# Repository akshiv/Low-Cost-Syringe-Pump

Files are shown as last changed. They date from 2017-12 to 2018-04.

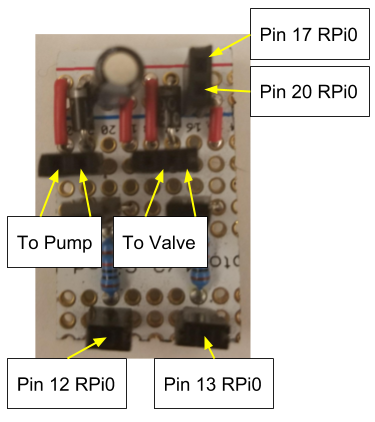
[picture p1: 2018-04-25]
documentation/figures/Driver Connections.png

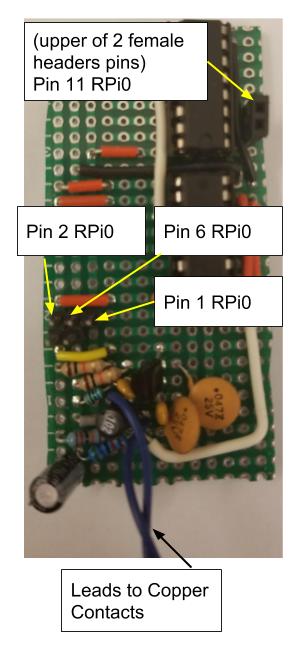
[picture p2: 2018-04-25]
documentation/figures/Oscillator Connections.jpg

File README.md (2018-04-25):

# Low Cost Syringe Pump
Repo for the ENPH 479 syringe pump project

## Introduction
This readme document serves as a guide to future development of the low cost syringe pump project. This document will outline the details of basic use and development. Further details on design approach and project motivation can be found in the engineering recommendation report for the project, which is located in this same git repository. 

## Getting Started with The Pump
The pump employs a Raspberry Pi Zero for controlling and powering all components. The first step for project development is to configure the Raspberry Pi for headless operation so that it can be controlled via Wifi. The pump’s electromechanical systems can then be setup, and the pump code can be ran on the raspberry Pi to operate the pump.

### Raspberry Pi Setup
The system uses a raspberry pi zero with pre-configured software loaded on the SD card so that the files needed to run the pump are available. 

To control the Raspberry Pi over wifi, the system must be setup to access the local wifi network by following step 3 of this tutorial document.

One can then connect to the Raspberry Pi using SSH either through the terminal on Linux, or by using a tool like PuTTY on Windows. Connect to the Pi at the adress pi@raspberrypi.local on port 22. The default password is raspberry

### Pump Setup
To connect all electrical connections in the pump system, follow this raspberry pi pinout chart, and the following diagrams which show the connections for the two pump circuit boards (the oscillator on the left and motor driver on the right).

The pneumatic connections between the pump, valve, and drive syringe must also be connected using a tee-junction. Then all components can be arranged within the 3d printed chassis and the two halves of the chassis can be secured together with elastic bands. 

### First Run

## Potential Future Projects 

### Feedback system design for a Low-Cost Syringe Pump for Global Medicine

#### Project Objectives, Background and Scope
The low cost syringe pump project is aimed at providing cheap accessible anesthesia in low resource surgical environments. The system uses capacitive contact feedback to improve accuracy and precision in lieu of mechanically precise components to bring down cost. An initial prototype, with a working capacitive contact/oscillator system exists but needs to be improved for both performance and reliability. The project will focus on designing the lowest cost oscillator, which can achieve the performance targets, improving the control loop so that the system can be used in a mission critical settings, and testing the reliability of both systems together. 

#### Design and Analysis
Design
Best possible oscillator used to amplify a variable capacitor scheme
Robust control loop which matches a flow rate based on oscillator input, desired pump rate, and current infusion status
Time permitting, sealing and packaging of electronic component inside of chassis for field deployment

Analysis
Reliability testing for both the control loop and the oscillator 
Edge case mitigation for errors/anomalies in clinical use

#### Expected Technical Background
Ideal candidates for this project will have an interest in circuit and control design. They will be comfortable using standard electrical prototyping equipment. They will be comfortable working in a Linux environment and writing code in C. 

### Smartphone Interface Development for a Low-Cost Syringe Pump for Global Medicine

#### Project Objectives, Background and Scope
The low cost syringe pump project is aimed at providing cheap accessible anesthesia in low resource surgical environments. The system uses capacitive contact feedback to improve accuracy and precision in lieu of mechanically precise components to bring down cost. To make the device as useful as possible we need it to be both powered by and operable using a smartphone. To achieve there needs to be an app which can allow an operate to set an infusion rate and volume and also receive feedback on the process. The smartphone will need to send this information via USB On the Go to a Raspberry Pi Zero, which will use it to actually drive the pump. Ideally, the app will allow phones to be swapped mid-procedure to allow for more lengthy infusions.

#### Design and Analysis
Design:
Setup a communication protocol using USB OTG, Android, and a Raspberry Pi Zero
Design an application which easily allows an operator to control and monitor an infusion process 
Create a system to allow the infusion to be carried out on multiple smartphone devices 

Analysis:
Assess reliability in case of various software/hardware failure on the smartphone side
Find edge cases present in the clinical environment and work to mitigate them
Reduce power consumption to make the circuitry last

#### Expected Technical Background
Ideal candidates for this project will understand development for Android devices, and be resourceful when working with communications devices.

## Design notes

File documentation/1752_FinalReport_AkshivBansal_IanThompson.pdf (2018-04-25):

## Development of a Low-Cost Syringe Pump for Low-Resource Anesthesia

## Akshiv Bansal Ian Thompson

## Project Sponsors: Dr. Mark Ansermino Dr. Guy Dumont

Applied Science 479
Engineering Physics
The University of British Columbia January 8th, 2018

Project Number: 1752

# Preface

There are no confidentiality considerations when reading this report. We thank the members of

the UBC Digital Health Innovation Lab, especially Dr. Mark Ansermino, Dr. Guy Dumont, Dr.

Richard Merchant, and Dr. Chris Peterson, for their support in this project.

Executive Summary Word Count: 235

Main Body Word Count: 3790

Akshiv Bansal | Ian Thompson

# Executive Summary

Safe surgical care is an essential medical resource which is unavailable to billions of people in

developing nations. Intravenous anesthesia plays a critical role in surgery, however conventional

syringe pumps are too expensive for widespread use in low-resource settings. To address this

issue, we developed a low-cost syringe pump using less than $25 of components. To meet the

demands of surgery, we aimed to achieve an accuracy of ±15% at drug delivery rates of 10-200

mL/hr.

The syringe pump design employs a simple 3D printed chassis, which holds two syringes back-

to-back. An air pump and valve drive one syringe, forcing anesthetic from the other syringe. Our

solution substitutes expensive precision components for feedback-based control. Inlaid copper

strips capacitively sense changes in the syringe volume, and a Raspberry Pi Zero uses this

feedback to control pumping and deliver anesthetic smoothly. The entire system runs from a

powered USB connection.

Testing over a wide range of flow rates, we found the pump met the design specifications for

infusion rate accuracy. This testing employed an analytical balance to track the flow of water

from the pump. These results demonstrate the viability of feedback-based syringe pump design

and provide a foundation for future development. Further refinement and validation of the

control algorithm will improve robustness and accuracy. Careful consideration of the surgical

environment and consultation with healthcare providers will help ensure successful deployment

of the device in field trials.

# Table of Contents:

Mechanical Drawings of Pump Chassis | 32
Connection Diagrams for System Setup | 33
Software Information for Project | 35

## List of Figures

Figure 1: System Overview for Feedback and Control | 9
Figure 2: Mechanical Chassis Design | 10
Figure 3: Electrical schematic layout of the Colpitts variable frequency oscillator | 11
Figure 4: Software Control Flow Chart | 13
Figure 5: Testing Setup for evaluating pump performance | 14
Figure 6: Oscillator Output Waveforms | 15
Figure 7: Capacitive feedback response linearity | 16
Figure 8: Syringe pump test results for a variety of flow rates | 17
Figure 9: Proposed UI for Android phone development | 25
Figure 10: Mechanical Drawing for Pump Chassis | 32
Figure 11: Colpitts Oscillator PCB with labelled connections | 33
Figure 12: Motor Driver PCB with labelled connections | 34

## List of Tables

Table 1: Summary of project expenses | 22
Table 2: General Bill of Materials | 27
Table 3: Oscillator Bill of Materials | 29

## List of Abbreviations:

FPGA | Field Programmable Gate Array
DHIL | Digital Health Innovation Lab (Project Sponsors’ Lab)
IC | Integrated Circuit
RPi0 | Raspberry Pi Zero

# Introduction

## Background and Significance

Anesthesia is an essential medical service, which induces paralysis or unconsciousness in the

patient, allowing for easier surgery and alleviating pain for patients. Intravenous anesthetics are

administered through injection into the patient. They are common and well-understood.

Conventional medical practice in developed nations employs a motor-driven lead screw to force

a precise flow of anesthetic from a loaded syringe.

In Essential Surgery, the International Collaboration for Essential Surgery outlines 44 procedures

that would avert 1.5 million deaths every year in developing countries, many of which rely on

pump-based IV anesthesia [1]. Existing commercial solutions are far too expensive for these

settings, costing $1000 or more. By designing a low-cost anesthetic pump, we aim to make these

critical procedures more available. Previous pump designs have showed promise for addressing

this need but have been inadequate in accuracy [2], versatility [3], or total cost [4]. We believe

that an innovative, closed-loop approach will allow us to address the need for accuracy while

maintaining a low device cost.

There are unique challenges we faced when designing a syringe pump for use in developing

nations, and constraints of the low-resource surgical environment have informed our project

goals and design decisions. Our primary constraint was cost. We focused on using commonly

available components and simple methods of fabrication and construction. We ensured that the

system will be cost-effective at initial deployment by choosing the most effective design for a

scale of tens to hundreds of pump units.

Another constraint is the lack of reliable, clean power in many surgical environments. We

designed our system to be powered from a mobile phone, which is a widespread and reliable

source of power. We designed our pump to have low latent power consumption, and to pull no

more instantaneous power than a typical mobile phone can provide. We considered other

variabilities in operating environments. Finally, we aimed to create an open source and easily

adoptable design. We created simple designs using common tools and programming languages, with the intent of making build plans available to groups who want to use the device. Versatility

in syringe size was considered to allow adaptation to different medical procedures.

## Project Objectives

1. Design of a syringe pump for approximately $25 in components or less
2. Demonstration of a syringe pump, which delivers anesthetic at a specified flow rate

between 10-200 ml/hour with an accuracy of ±15%.

3. Design of an electrical power and user interface system to allow the pump to be operated

and powered directly from an Android mobile phone.

4. Design of mechanical and electrical systems to ensure the syringe pump is operable

without expertise, while being tolerant to light impacts, dust, water, and variations in the

environment.

5. Appealing implementation of the system so it can be demonstrated to potential sources of

funding or other parties interested in supporting the project.

## Report Scope and Organization

To effectively deliver anesthesia, we sought to build a closed-loop, pneumatically-actuated

pump, with a capacitive feedback mechanism. We started the project with a syringe pump

concept, which worked using an FPGA and a specific syringe model. Throughout the project we:

designed and built a new chassis to work with any generic syringe, created a new electronic

measurement and control system using feedback electronics and a Raspberry Pi Zero computer

(RPi0), and validated the pump performance at a variety of flow rates.

The project excluded consideration of alternative feedback mechanisms, controllers, and

actuation methods. These were excluded because of time constraints and increases to the final

cost of the device. For example, the FPGA was abandoned because at the scale of our initial

device production, the chip setup would be more expensive than the RPi0 solution. These topics

will not be addressed in this report.

# Discussion

## Methods

System Design

The system is composed of three subsystems: a RPi0 controller, an air pump/valve pneumatic

actuation system, and a capacitor-controlled oscillator for feedback. The feedback system is used

to obtain information on the syringe position, which is processed by the RPi0 controller to

generate pneumatic correction to achieve proper drug delivery rates. The pneumatic corrections

are applied by actuating the air pump/valve system.

These systems are all housed in a single 3D-printed chassis to create a clean and compact

prototype. Power to run the device is provided by an Android phone. All aspects of the system

are intended to limit upfront cost and allow for use with minimal additional materials. The

intention is to deliver a kit with everything required to run the pump out of the box, save for a

soldering iron, medical tubing, a syringe, and a smartphone. Pneumatic actuation and capacitive

feedback help to reduce the material cost significantly by alleviating the need for precision

actuation components. Cost was the driving factor many design decisions, including selection of

all electronic and electromechanical components. The total cost of the project is estimated to

approximately $23.50. The RPi0 enables ease of development in C and allows a wider open-

source community to adopt and change the project.

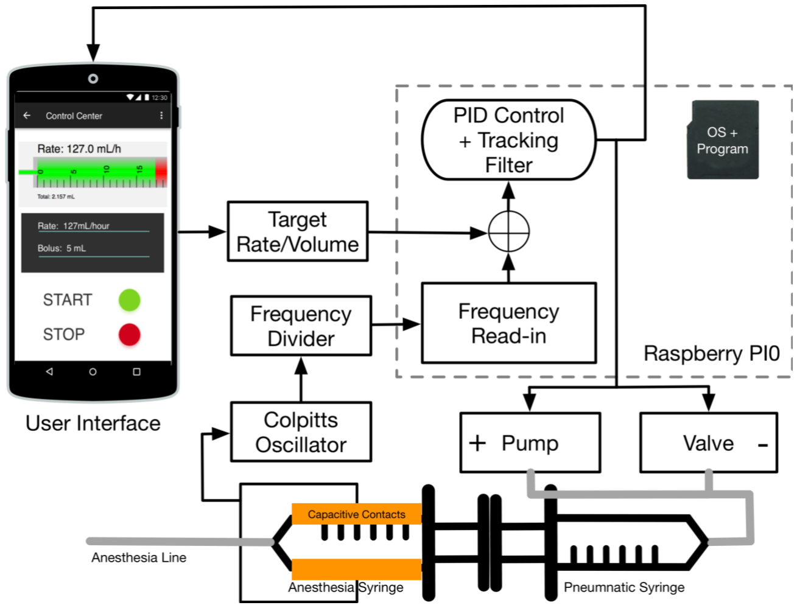
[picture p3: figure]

Figure 1: System Overview for Feedback and Control Using the smartphone, the user inputs a target infusion rate and an overall volume. The rest of the system responds to deliver anesthetic as specified. The Raspberry Pi0 takes user input and issues signals to the pump/valve combination, driving the passive pneumatic syringe plunger forwards. The pneumatic syringe presses the plunger of the active anesthesia syringe, which dispenses the drug solution through the anesthesia line. Copper contacts on either side of the syringe form a capacitor, which set the frequency of a Colpitts oscillator. This signal is frequency divided and read into the Raspberry PI0 as feedback for a PID control algorithm, which in turn actuates the pump/valve system

Mechanical Design

The chassis is designed to house all of the components and provide resistance to impact. To this

end, the design focused on making an economically printable enclosure, with a setup to allow all

electronics to be installed in the body, without need for electronics access or adjustments during

operation.

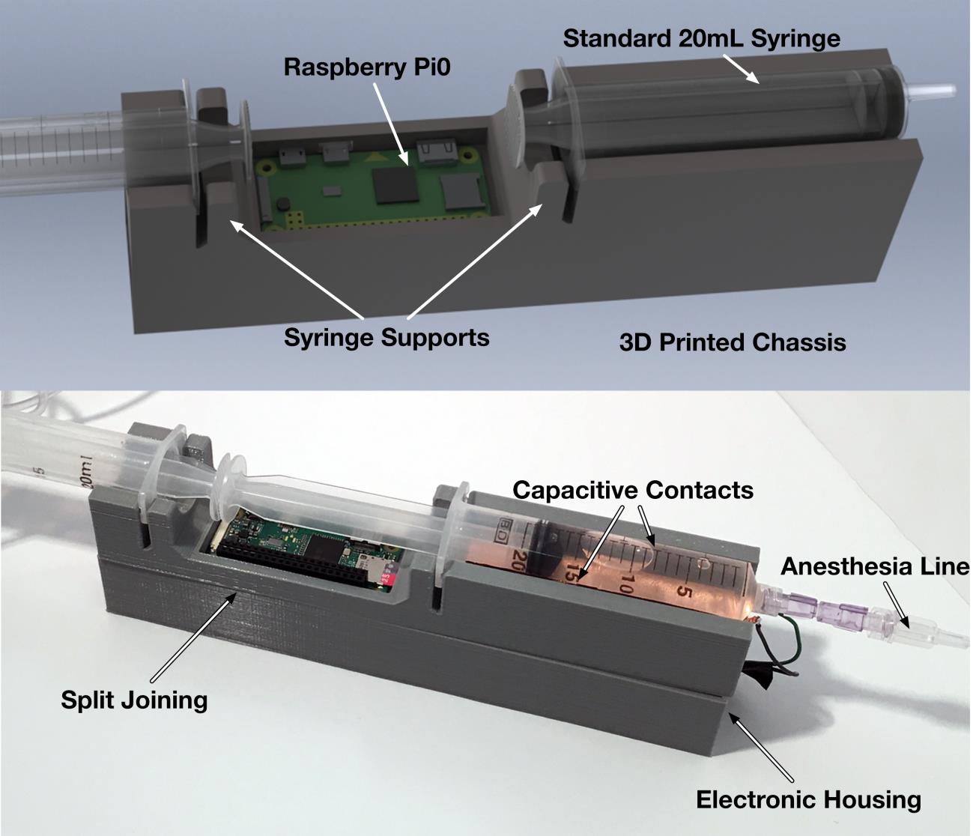
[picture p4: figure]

Figure 2: Mechanical Chassis Design The chassis design is based on original work done by the project sponsors. This chassis has built in capacitive contact pads, such that generic anesthetic syringes can be used, and a clean surgical setting maintained. All of the electronics are housed inside the chassis, and the Raspberry Pi0 sits below the syringes (normally covered). The split in the prototype was introduced to simplify 3D printing, and the two halves are joined. The syringe supports are necessary to deal alternating stress from syringe installation and operation.

Electrical Design

To accurately detect small capacitance changes due to syringe actuation, we constructed a

capacitance-controlled variable frequency oscillator. We selected the Colpitts oscillator topology

(shown in Figure 3), which produces large variations for small capacitance changes, and uses

readily available, affordable components. Each oscillation must be accurately detected by the

RPi0, thus we tuned component values to adjust the signal amplitude and frequency to match the

RPi0’s capabilities. We found a maximum detectable frequency of 18kHz for our read-in method

on the RPi0, limited by I/O bus speed. A two-stage, 18-bit frequency divider reduces the

oscillation frequency to approximately 100 Hz, lowering the computational demand with

minimal component cost.

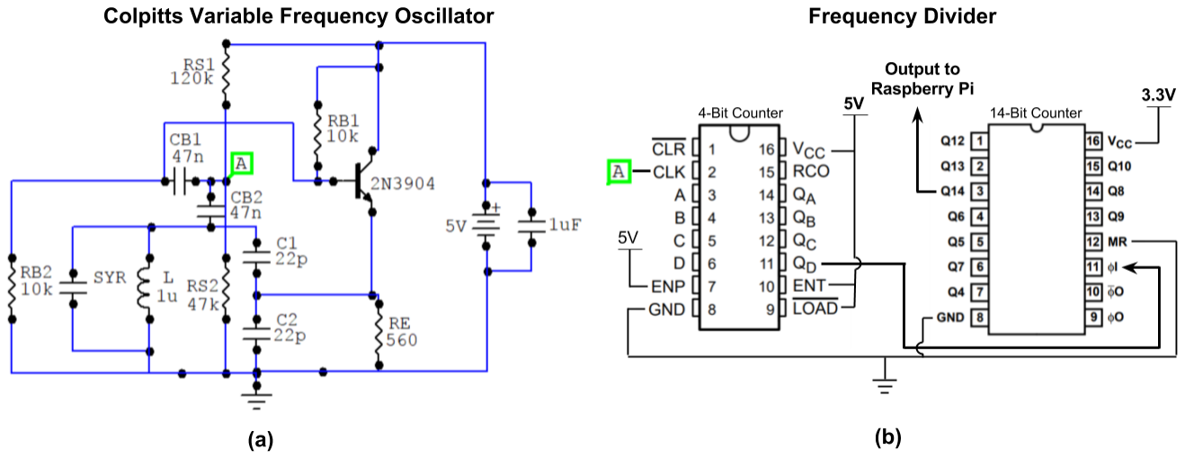
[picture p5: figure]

Figure 3: Electrical schematic layout of the Colpitts variable frequency oscillator
(a) A variable frequency colpitts oscillator topology is used to create a sinusoidal oscillation at point A (labelled with a green square). Variations in the syringe capacitance (labelled SYR in the diagram), change the oscillation frequency. The frequency is in the range of 30-50 MHz, set by L, C1 and C2. We selected setpoint-biasing resistors and bypass capacitors (RS1, RS2, CB1 and CB2) to center the oscillation around the correct voltage for input into a frequency divider circuit. (b) A frequency divider circuit uses a 4-bit and a 14-bit counter to divide the oscillation frequency, allowing for output to the Raspberry Pi 0. Separate Vcc for each counter are selected to ensure the correct output voltage range.

The air pump and valve are operated using general purpose input/output (GPIO) pins on the

RPi0. Since the GPIO pins have a output current lower than needed to drive the system, we

constructed a simple switching circuit using an NPN Darlington transistor to power the

components from the device power rails. The GPIO pins control switching; for logic high, the

driver circuit powers the air pump or valve with 3.3V, and for logic low, the component is

switched off.

## Flow Diagram / Algorithms

The pump control is code executed on the RPi0 and is initialized by the user providing a target

flow rate and total volume. Feedback from the syringe is monitored using an interrupt routine,

which counts oscillations for a developer specified counting interval. Shorter counting intervals

can be selected to increase response time, while longer intervals improve noise rejection. As readings are constantly generated by the feedback system, these values are compared to user

targets for flow rate.

The control system actuates the valve and air pump in response to error, increasing or decreasing

the air pump driving voltage if the syringe is lagging or leading respectively, or opening the

valve when the syringe is moving too fast. The developer can specify weights for proportional,

integral, and derivative error, as well as the threshold for releasing pressure through the valve.

These parameters can be tuned to optimize system performance. The syringe pump runs until the

feedback indicates that the system has infused the total amount desired, at which point the pump

stops and releases all pneumatic pressure. During the pumping process, the feedback readings,

pumping status, and applied valve and air pump corrections are reported for analysis. The code is

implemented in C for speed and ease of execution on the RPi0.

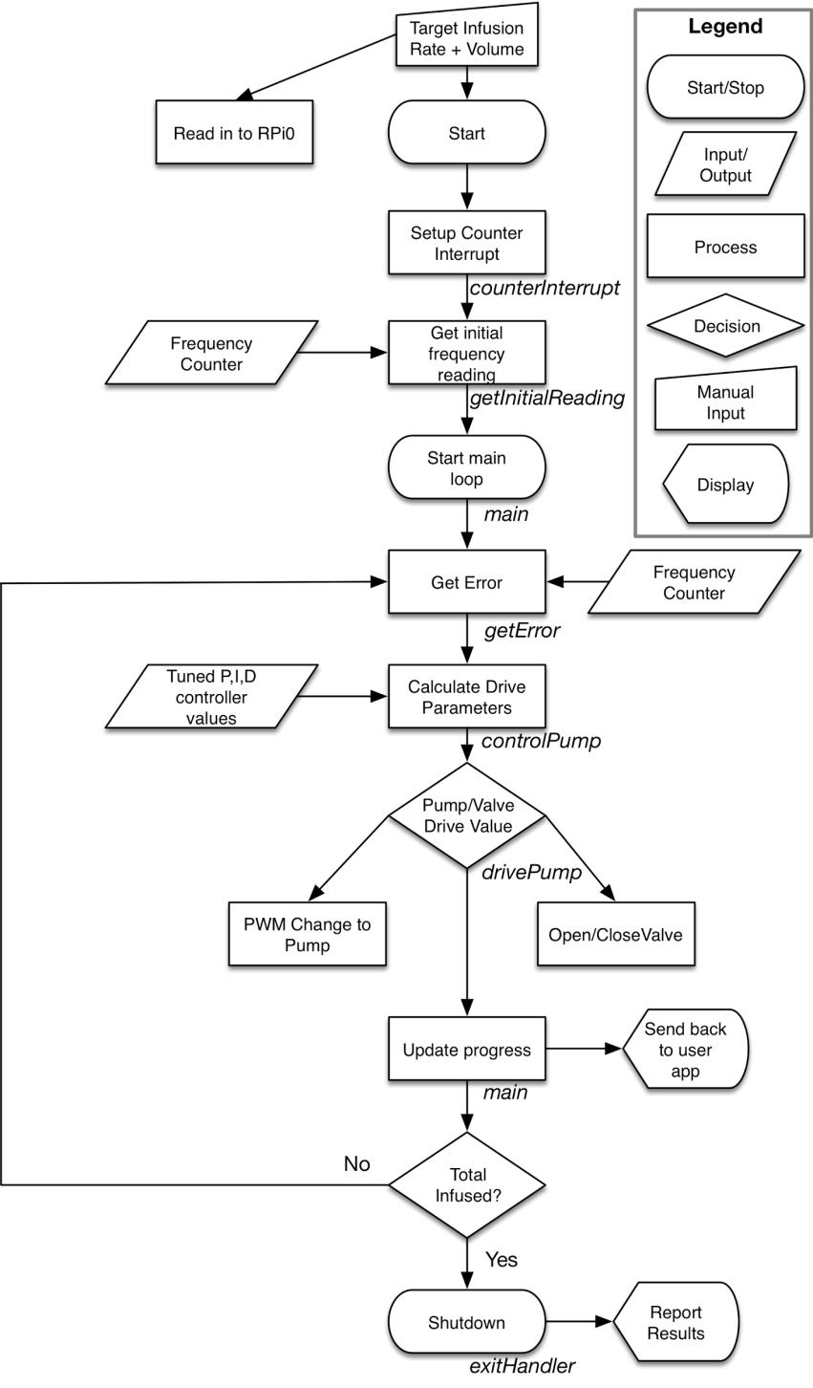
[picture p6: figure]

Figure 4: Software Control Flow Chart The software implementation on the Raspberry Pi0(RPi0) handles pump control, with an Android app serving as the user interface. After the user sets the target rate and volume, the RPi0 initializes its I/O ports, and starts to read in frequency information from the oscillator/capacitor feedback system. The system stays in its primary loop until the desired amount of drug has been infused. In the loop, the system generates an error from the difference in the current syringe position and the desired syringe position. It then uses this error, along with control parameters, to drive the pump faster or slower, release the check valve, or wait until the next update. Upon reaching the volume target or encountering an error, the system goes to the exit handler, which stops all parts of the system before reporting the result to the operator and shutting down the system.

## Experimental Equipment & Testing Protocol

We characterized the Colpitts oscillator output using an oscilloscope, powering the circuit from

the RPi0. Capacitive feedback linearity data was obtained using the same frequency counting

routine as the pump control software.

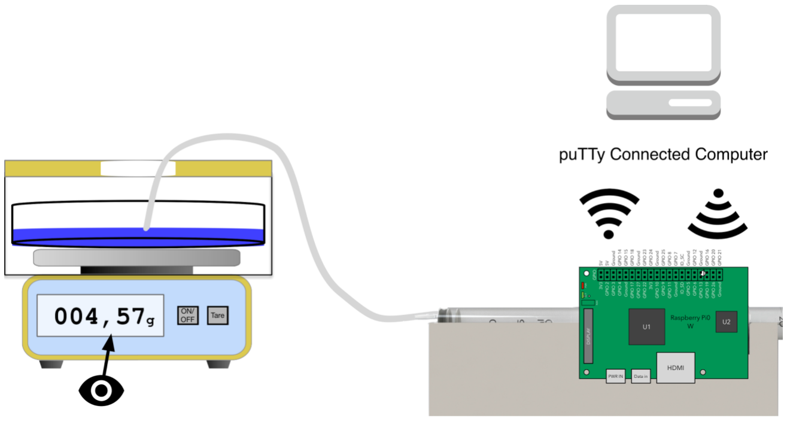
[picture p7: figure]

Figure 5: Testing Setup for evaluating pump performance We used an analytical balance to test the infusion accuracy of the syringe pump. A computer linked to the Raspberry Pi Zero (RPi0) via an SSH connection was used to issue pump commands. We tested multiple infusion rates and volumes, monitoring the progression of each infusion. We set the pump up to drip through medical tubing into a plastic dish on top of an analytical balance (Sartorius BP110). To ensure minimal evaporation and variability we zeroed the balance with 20 mL of water already in the dish and used a plastic cover to minimize airflow. The data from the display on the balance was manually recorded at 1-minute intervals. All components were powered using AC wall power with a common ground.

We took pump performance data using an analytical balance to best replicate the ISO standard

testing protocol (detailed in Appendix: ISO Standard for Syringe Pumps). This setup is less

rigorous than the standard requires but provides a useful benchmark with the apparatuses we had

available.

## Results

The output signal from the finalized Colpitts oscillator design is shown in Figure 6 along with

the frequency divided square wave, which is input to the RPi0. The circuit was powered from the

RPi0, and waveforms were collected for a typical syringe loaded with 20 mL of water. We

designed the Colpitts oscillator with small capacitive and inductive components to increase the

sensitivity to changes in the syringe capacitance. This resulted in a high oscillation frequency of

43.91 MHz measured at the oscillator output (top subfigure). This waveform is nearly sinusoidal,

with some distortion likely due to secondary resonances in the circuit. Our frequency divider was

successful in generating a low-frequency output (bottom subfigure) to trigger the RPi0, reducing

the oscillation to 116.4 Hz and rectifying the signal to a 0-3.3V square wave with minimal

distortions or noise.

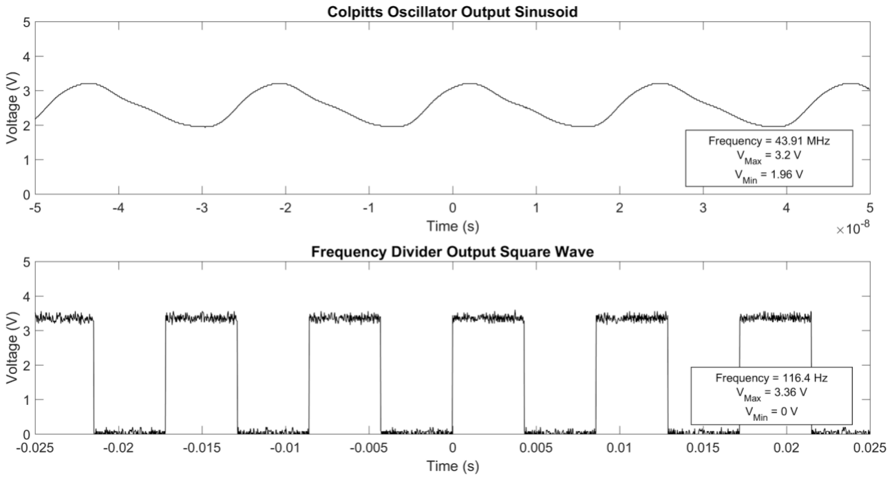
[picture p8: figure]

Figure 6: Oscillator Output Waveforms We collected output waveforms of the Colpitts oscillator before and after the frequency divider using a fully loaded syringe. Top: The signal measured at the output of the Colpitts oscillator before the frequency divider (position A in Figure 3). The initial circuit has a high frequency (43.91 MHz) output sinusoid, with a small voltage swing. Bottom: The signal measured at the final output to the RPi0. The frequency divider circuit amplifies the low-voltage sinusoid to a 0-3.3V logic signal and reduces the frequency to 116.4 Hz so that it can be properly detected by the RPi0.

To simplify the controls, we assumed the changes in feedback readings would change linearly

with the fluid volume in the syringe. To validate this assumption, we manually varied the volume of fluid through the functional range of 20mL syringe, sampling the feedback readings using the

RPi0. Performing a linear fit in MATLAB (shown in Figure 7) we find that the linear

approximation matches our data well within our desired pumping accuracy. Over the 20 mL

range of the syringe, we note a 1.84% change in the feedback readings.

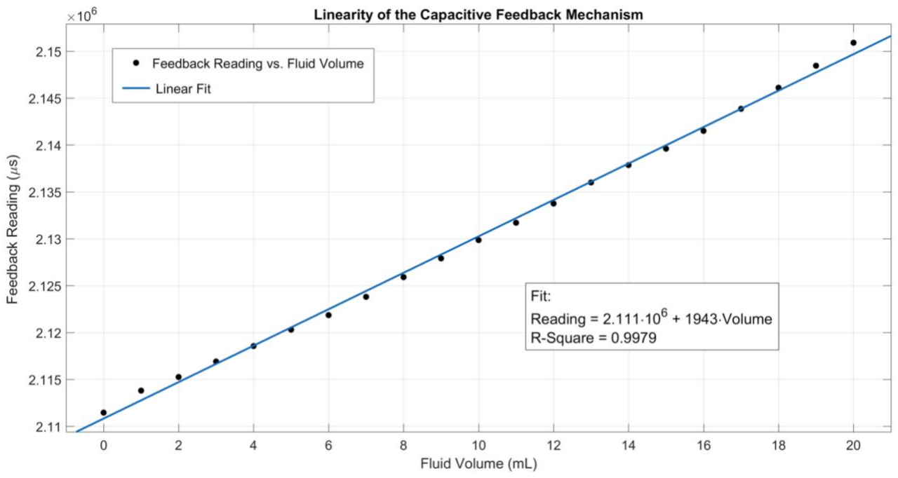
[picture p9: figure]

Figure 7: Capacitive feedback response linearity We obtained feedback readings by measuring the output period of the Colpitts variable frequency oscillator across the range of syringe fluid fill volumes. A linear fit approximates the data with an R-Square value of 0.9979, demonstrating that the feedback response is sufficiently linear over the desired operation range. This linearity can be used to simplify our control scheme and accurately approximate volumes and flow rates delivered by our system.

Using our linear feedback mechanism, we tested our PID control scheme at a variety of target

flow rates, following the procedure laid out in Experimental Equipment & Testing Protocol.

Figure 5 shows the pumping results when the pump was configured to deliver a specified total

volume of water, stopping when it sensed it had pumped that amount. The control system ran

with only proportional control, a limit of ~40% on the maximum pumping power, and a feedback

update period of approximately two seconds. At almost all time points, the pump delivered the

correct volume to within ±15% (as shown by the dotted bounds in the figure). It monitored the

total volume infused and stopped within 15% of the final target in 3 of 4 trials. During all trials,

the pump ran independently with no operator intervention.

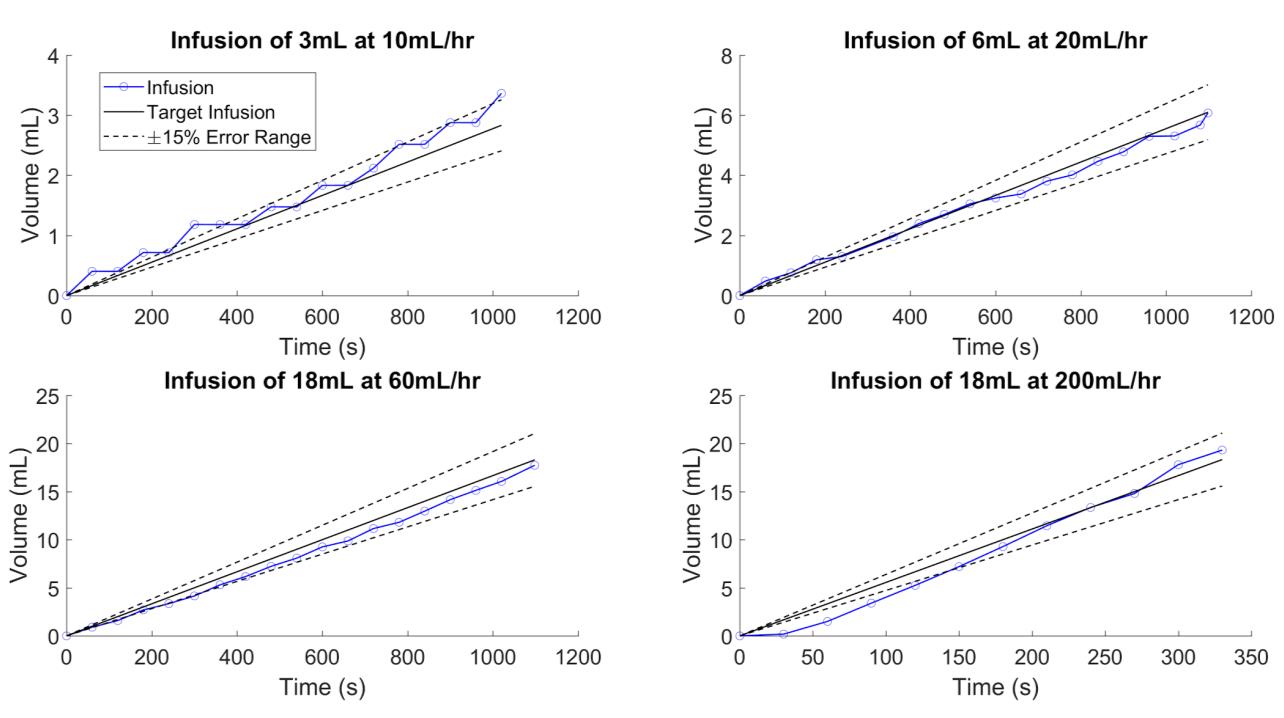
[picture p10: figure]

Figure 8: Syringe pump test results for a variety of flow rates The accuracy and smoothness of delivery for our syringe pump was tested by pumping water onto an analytical balance at a range of specified rates until a specified target volume was reached. The pump was run using proportional control, updating the control response every ~2 seconds. Flow rates of 10, 20, 60, and 200 mL/hr were selected to be representative of the full range of flow rates we expect our pump to deliver. Blue lines with circles denote the resulting volume infused by our pump (calculated assuming 1g/mL water density). The solid black line denotes the target infusion rate while the ±15% volume accuracy we aim to achieve is given by the dotted lines. Our pump meets our accuracy criteria for the majority of flow rates tested, however the presence of stiction leads to rougher performance in very slow pumping, seen in the step-like plot for 10 mL/hr infusion.

## Discussion of Results

The Colpitts oscillator outputs a reliable, well-formed signal to communicate feedback to the

RPi0, however robustness of the output can be improved. The voltage oscillation from 1.96 to

3.2 V is sufficient to be detected as input to the frequency divider circuit, however variations in

syringe capacitance or supply voltage may decrease the amplitude to under the detection

threshold. It was noted in some cases that oscillations could be lost if the syringe was improperly

placed or connections were loose. Modifications to buffer or increase the amplitude of the high-

frequency oscillator output, to improve connections, or to shield the circuit from outside static or

fields from the pump and valve may increase reliability. The counting ICs allowed for simple

reduction of frequency, making the feedback signal suitable for read-in to the RPi0, however this

leads to a reduction in precision when counting numbers of oscillations. We believe this approach is satisfactory for our control system. Increasing the precision may enable lower flow

rates to be delivered more accurately.

We can use the linearity of our feedback system response to simply and reliably monitor the

position of the syringe plunger, providing information on anesthetic flow rate and total volume

delivered. However, because the total change in readings over the range of the syringe is only

1.84%, and because we often deliver quantities smaller than the 20 mL full range, the sensitivity

of our feedback method may pose an issue. For very slow flow rates, the desired changes in

feedback readings can be very small, with noise posing a significant challenge to precision. The

15% pumping accuracy target affords some inaccuracy; however, the noise sensitivity

necessitates careful design of the control algorithm to reject noise.

The pumping performance suggests that our simple PID control algorithm is sufficient for

achieving volumetric accuracy to within 15% during infusion. While the pump exceeds the error

bounds at a few points, further testing and refinement of the control algorithm and parameters

may lead to consistent accuracy.

The pump system appears to perform best at flow rates in the middle of the specified range of

10-200 mL/hr. Because of stiction, the pump delivered anesthetic in small discrete increments,

rather than at one constant flow rate, alternating between idling and pumping somewhat rapidly.

This behavior can be seen in the step-like performance at the lowest flow rate (10 mL/hr) where

the quantity delivered per minute is so small that periods of idling last longer than one data point.

For all tests, and especially those at high flow rates, the pump showed more significant error at

the beginning of infusion, likely due to errors in estimating the initial position at startup, or

delays in pumping to an operational air pressure.

Several control system changes could be tested to correct for these issues. The lengthy feedback

update period of two seconds may be reduced to increase response time, leading to smaller step-

like increments and overall smoother behavior. However, reducing this time may lead to

increased noise sensitivity at low flow rates. Another approach to increasing smoothness may be

to lower the maximum power limit, however this may limit the pump’s ability to overcome obstructions in the line. A more robust solution could be varying the output power limit based on

the desired flow rate, as this may compensate for both the pulsing at low flow rates and the

startup inaccuracies at high flow rates. With careful adjustment and testing of the control

algorithm, we are confident that we can reliably achieve our accuracy target at all flow rates.

# Conclusions

We have successfully demonstrated a novel feedback mechanism for monitoring syringe position

during pump operation. Using capacitive sensing and a Colpitts oscillator circuit, we generate a

frequency signal, which varies with the syringe position. By demonstrating consistent linearity of

the feedback response, we showed that this system can monitor and adjust the drug delivery

process, increasing accuracy. This development represents a fundamental difference from other

syringe pumps, which rely only on precision components and open loop control.

Our pumping approach has been implemented with a compact and easy to use design. The

selection of a 3D-printed chassis allowed for easy integration of capacitive contacts, secure

housing of pump components, and design reproducibility. All components were constructed with

easily available parts, for a total parts cost of ~$23.50 (see Bill of Materials in Appendix for cost

breakdown). We believe these design choices will encourage interest in our proof of concept

device and attract potential funding or continued development efforts.

Our device achieved pumping accuracy to within ±15% over our desired range of flow rates

from 10-200 mL/hr. This performance shows that our first proof of concept merits further

development and design refinement. The main barrier to adoption of our device for clinical use is

its reliability and complexity of use, and this must be addressed going forward. Adjustments to

the control scheme may increase accuracy for low and high flow rates. Sophisticated knowledge

of the project is needed to construct and operate the device in its current state. Our

recommendations aim to finalize the device in a form more suitable for widespread use.

# Project Deliverables

## List of Deliverables

1. Mechanical and Electrical Design files
a. Includes all documentation, design work, and component lists that would be

needed to make the pump at scale (i.e. at the desired $25 price point)

b. The designs are delivered in a “manufacturing ready” form
c. Documented sufficiently to allow for greater extensions/improvements

We will deliver these files to the project sponsors. The manufacturing readiness of the project is

not as expansive as originally forecasted. Additional units will still need to be 3D printed instead

of injection molded. Electronics will need to be assembled on prototype PCB, not outsourced to

a PCB manufacturer. All electronic design files will be available in the same public GitHub

repository as the software.

2. Physical Prototype Syringe Pump
a. Delivery of a working syringe that has a volumetric accuracy of ±15% and

performs in the flow rate range: 10-200mL/h

b. The prototype has a polished design
- Electronics are not visible
- Mechanical chassis is sealed
- Design can deal with modest shocks
c. The prototype can run off an Android phone for at least 2 hours, and is operable

through simple GUI

d. Moisture and splash proofing of the pump, including protecting electronics.

The prototype meets our specified accuracy over the desired range of flow rates. The chassis is

stronger and lighter than before, all components can be nicely fit together and displayed. The

chassis is not sealed or splash-proof. While the prototype will be powered by an Android phone

after our ongoing commitments are fulfilled, it cannot yet be operated by one. We will schedule a

handoff meeting where we will give our sponsors two 3D printed bodies, one with the working

pump inside. The prototype will be setup to give demonstrations and is easily configurable for

further validation.

3. Final Documentation (including Engineering Recommendation Report)
a. Includes all design documentation and methods used
b. Includes all results from prototype validation
c. Includes a list of recommended improvements before field testing

This report meets this deliverable as intended. During the hand-off meeting we will determine if

an operating manual is required, and what its requirements are (discussed in Ongoing

Commitments).

4. Access to code developed for running the syringe pump

Our open-source GitHub repository contains readable code, instructions for compiling/building,

and allows for reproduction and modification.

## Financial Summary

Item | Quantity | Vendor | Unit Cost | Purchaser | Note
3D Printing Services | 1 Pump Chassis Print | ECE Student Services | $39.20 | Guy Dumont | Sponsor’s ECE Speed Chart
4-Bit Counter SN74F163AN | 5 | Digikey | $0.95 | Project Lab | Project lab Funds
14-Bit Counter CD74HC4060E | 5 | Digikey | $0.87 | Project Lab | Project lab Funds

Table 1: Summary of project expenses At the resolution of the project, no funds are owed between parties. All other project materials not listed below were provided by project sponsors or the engineering physics project lab but not purchased specifically for this project.

## Ongoing Commitments

1. Project debrief meeting - Akshiv & Ian, End date: Mid-Feb
- We will meet with the sponsors to demonstrate our final pump performance and

discuss the future of the project.

2. Establishing Android phone powering of syringe pump - Akshiv, End date: March 8th

- Finish development of an app to allow the pump to run from a mobile phone. The

pump should be able to run without intervention for 2 hours.

3. Creation of an operation/development manual - Akshiv & Ian, End date: April 1st
- The requirements will be determined in the handoff meeting. This work is

intended to take a maximum of one week

4. Improvements to prototyping quality - Akshiv & Ian, End date: Feb 15th
- Finishing Solidworks model to include modest sealing of chassis (12 hrs. effort)
- Clean up internal wiring and connections (6 hours effort)

# Recommendations

## 1. Better securing of syringes and other components

The chassis presently features no good mechanism to secure the syringes firmly into the chassis.

This could be done by attaching elastic bands over the syringes or some change in the

mechanical design of the chassis. Implementing this will improve the reliability of the system

and allow more reliable contact between the inlaid capacitive contacts and the syringe. Further,

the electronics within the chassis could be better secured to prevent shocks from affecting system

performance. This could be done using adhesives, slots, fasteners, or other mechanical redesigns.

## 2. Further control tuning and performance validation

The pump performance provided a valuable proof of concept, but the control system needs

refinement to increase reliability and versatility. We recommend testing the effects of shortening

the feedback response time or adjusting the maximum pump power limit based on flow rate.

These adjustments may improve the pump accuracy beyond our current limits. Repeated testing

of the pump for consistency between infusions is also valuable. The pump should also be tested

with a variety of outlet attachments on the end of the anesthetic line to simulate infusion in a

clinical setting. Significant fluid resistance or back-pressure may be introduced when a needle,

adapter, or live patient is added into the fluid line. These scenarios should be carefully

considered and tested.

The robustness of the device to real-world operating conditions should be evaluated by

introducing factors such as large temperature changes, vibrations, movement of the pump body,

and interfering electromagnetic fields (i.e. nearby motors). A successful design will be

unaffected by these factors, and these issues may necessitate mechanical or electrical

modifications. Possible failure modes and misuse during operation should be investigated, such

as power disconnection, loss of communication to the device, or accidental operator input. These

cases may lead to considerations of fail-safes in software. Testing all these possible cases will

ensure that the system is fit to be used in the clinical setting. The final validation process must be

done in consultation with low-resource health care providers.

## 3. Mobile UI

To allow full deployment of the pump in the field, an Android app to operate the pump should be

created. The scope of this project entailed creating and app to power the pump from a phone,

however we did not consider phone-based operation by a healthcare provider. This user interface

needs to enable the operator to set flow rates and target volumes, to start and stop the pump, and

to monitor anesthetic delivery.

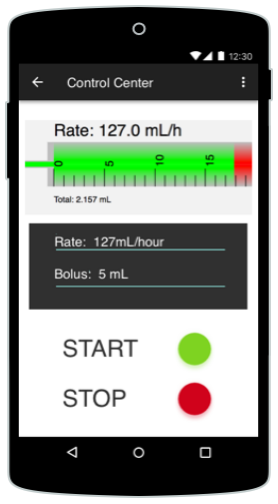
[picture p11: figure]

Figure 9: Proposed UI for Android phone development The UI allows the operator to set the target volume and infusion rate, monitor the infusion progress, and most critically start/stop the infusion.

## 4. Field Validation and Scaling Up

To develop this concept further we recommend first testing the system as designed on a small

scale in the field. The current approach using a RPi0 has been developed for optimal cost

effectiveness at small scale. After completing the recommendations, a field test with <100 units

is needed to verify the validity of using this device in a surgical setting. Once lessons learned in

field deployment have informed design modifications, the project can proceed to design for

larger scale. The device can be made more affordable and reliable through redesign for large

scale production. This involves designing a permanent PCB with an integrated FPGA, updating

the mechanical design to allow for injection molding, and creating an injection molding mold.

# References

[1] Essential Surgery. Washington (D.C.): World bank group, 2015. Print.
[2] Wijnen B, Hunt EJ, Anzalone GC, Pearce JM. Open-Source Syringe Pump Library. PLoS

ONE 2014 9(9): e107216. doi: 10.1371/journal.pone.0107216

[3] Mundle S, Regi A, Easterling T, Biswas B, Bracken H, Shekhavat DR, Durocher J, Winikoff
B. Treatment approaches for preeclampsia in low-resource settings: a randomized trial of the

Springfusor pump for delivery of magnesium sulfate. Pregnancy Hypertens. 2012;2:32–38.

[PubMed] (https://www.ncbi.nlm.nih.gov/pubmed/26104987)

[4] Juarez, Alexa et al. “AutoSyP: A Low-Cost, Low-Power Syringe Pump for Use in Low-

Resource Settings.” The American Journal of Tropical Medicine and Hygiene 95.4 (2016): 964–

969. PMC. Web. 7 Sept. 2017.
[5] CAN/CSA-C22.2 No. 60601-2-24:15; Medical electrical equipment — Part 2-24: Particular

requirements for the basic safety and essential performance of infusion pumps and controllers.

CSA Group, Mississauga ON.

# Appendices

## Bill of Materials

| Component | Vendor | Manufacturer | Source | Minimum Order | Cost (USD) | Quantity | Lead Time
1 | Solenoid Valve | EBay | bonk*town | A. | 1 | 1.59 | 0 | 2 months
| | | maaqii | B. | 1 | 1.63 | 1 | 1 month
2 | Diaphragm Pump | Aliexpress | DIT | C. | 10 Pieces | 2.419 | 0 | 20 Days
| | | SAILFLO | D. | 1 | 2.66 | 1 | 20 Days
3 | Darlington Transistor | Digikey | | E. | 100 | 0.1713 | 2
4 | 10uF E. Cap | Digikey | | F. | 1 | 0.22
5 | 1k Resistor | Digikey | | G. | 1 | 0.1
6 | Diode | Digikey | | H. | 100 | 0.0914 | 2
7 | Raspberry Pi 0 | | | I. | 1 | 5 | 1
8 | 2gb microSD | Aliexpress | | J. | 10 | 3.5 | 1 | 20 days
9 | USB Cable | | | L. | 1 | 0.6 | 1 | 40 days
10 | Oscillator Circ | | See below | | 1 | 2.85 | 1
| | | | Total: | | 16.96
| | | | Total (CAD) | | 23.50

Table 2: General Bill of Materials
A. http://www.ebay.com/itm/Mini-2-Position-3-Way-Electric-Control-Solenoid-Valve-Gas-Air-Pump-DC-

5V-6V-

HM/232395417786?_trkparms=aid%3D222007%26algo%3DSIM.MBE%26ao%3D2%26asc%3D41376%

26meid%3D6d133a7f9853490099fb0b4b447a6d6e%26pid%3D100623%26rk%3D2%26rkt%3D6%26sd%

3D122609196665&_trksid=p2047675.c100623.m-1 (http://www.ebay.com/itm/Mini-2-Position-3-Way-Electric-Control-Solenoid-Valve-Gas-Air-Pump-DC-5V-6V-HM/232395417786)

B. http://www.ebay.com/itm/Mini-2-Position-3-Way-Electric-Control-Solenoid-Valve-Gas-Air-Pump-DC-

5V-6V-MA-/112403400789?hash=item1a2bc3c855:g:rJAAAOSwIaFZFCDa (http://www.ebay.com/itm/Mini-2-Position-3-Way-Electric-Control-Solenoid-Valve-Gas-Air-Pump-DC-5V-6V-MA-/112403400789)

C. https://www.aliexpress.com/item/10pcs-New-370-DC-Air-Pump-370-motor-3V-dc-450mA-Oxygen-pump-

Mini-air-Pump/32728832531.html (https://www.aliexpress.com/item/10pcs-New-370-DC-Air-Pump-370-motor-3V-dc-450mA-Oxygen-pump-Mini-air-Pump/32728832531.html)

D. https://www.aliexpress.com/item/DC-6V-Mini-Air-Pump-Motor-For-Aquarium-Tank-Oxygen-Circulate-Durable/32830199091.html?traffic_analysisId=recommend_2088_2_90158_iswistore&scm=1007.13339.90158.0&pvid=f1234509-bb2c-48b8-8bce-fdf48264d68d&tpp=1 (https://www.aliexpress.com/item/DC-6V-Mini-Air-Pump-Motor-For-Aquarium-Tank-Oxygen-Circulate-Durable/32830199091.html?tpp=1)
E. https://www.digikey.ca/product-detail/en/fairchild-on-semiconductor/KSP13TA/KSP13TACT-ND/4314808 (https://www.digikey.ca/product-detail/en/fairchild-on-semiconductor/KSP13TA/KSP13TACT-ND/4314808)

F. https://www.digikey.ca/product-detail/en/micro-commercial-co/1N4007-TP/1N4007-TPMSCT-ND/773694
G. https://www.digikey.ca/product-detail/en/panasonic-electronic-components/ECA-1EM100B/P19522CT-ND/6109420 (https://www.digikey.ca/product-detail/en/panasonic-electronic-components/ECA-1EM100B/P19522CT-ND/6109420)
H. https://www.digikey.ca/product-detail/en/stackpole-electronics-inc/CF14JT1K00/CF14JT1K00CT-ND/1830350 (https://www.digikey.ca/product-detail/en/stackpole-electronics-inc/CF14JT1K00/CF14JT1K00CT-ND/1830350)
I. Various sources Canakit, Adafruit, etc.
J. https://www.aliexpress.com/item/10Pcs-Lot-64MB-128MB-256MB-512MB-1GB-2GB-4GB-8GB-TF-Card-Micro-SD-Cards-Micro/32819257976.html?ws_ab_test=searchweb0_0,searchweb201602_3_10152_10065_10151_10130_10068_10344_10345_10342_10343_10340_10341_10139_10307_10060_10155_10154_10056_10055_10054_10537_10059_10536_10534_10533_10532_100031_10099_10338_1 0103_10102_10052_10053_10107_10050_10142_10051_10084_10083_10080_10082_10081_ 10178_10110_10111_10112_10113_10114_9998_10312_10313_10314_10078_10079_10073-9998,searchweb201603_17,ppcSwitch_5&btsid=43012fd7-ad1e-40bb-a59ea7a1af898e6a&algo_expid=b0101ad3-e1b2-47fc-b655-c3a5fa6c4e23-0&algo_pvid=b0101ad3-e1b2-47fc-b655-c3a5fa6c4e23 (https://www.aliexpress.com/item/10Pcs-Lot-64MB-128MB-256MB-512MB-1GB-2GB-4GB-8GB-TF-Card-Micro-SD-Cards-Micro/32819257976.html)
K. https://www.aliexpress.com/item/Microusb-To-Female-USB-Host-Cable-OTG-Adapter-for-Lenovo-Xiaomi-Lg-Tablet-Android-Reader-Cabo/32670313423.html?ws_ab_test=searchweb0_0,searchweb201602_3_10152_10065_10151_10130_10068_10344_10345_10342_10343_10340_10341_10540_10139_10307_10060_10155_10154_10056_10055_10054_10539_10538_10537_10059_10536_10534_10533_100031_10099_10103_10102_10052_10053 _10107_10050_10142_10051_10325_10084_10083_10080_10082_10081_10178_10110_10111_10112_1 0113_10114_10312_10313_10314_10078_10079_10073,searchweb201603_2,ppcSwitch_5&btsid=62edbd e3-9e9e-4d37-ad84-00e080925017&algo_expid=828e3520-3206-4af5-9767-4ca5c9219ef5-0&algo_pvid=828e3520-3206-4af5-9767-4ca5c9219ef5 (https://www.aliexpress.com/item/Microusb-To-Female-USB-Host-Cable-OTG-Adapter-for-Lenovo-Xiaomi-Lg-Tablet-Android-Reader-Cabo/32670313423.html)

Oscillator Circuit Bill of Material
| Component | Vendor | Source | Minimum Order | Cost (USD) | Quantity
1 | 10k Resistor | Digikey | A. | 250 | 0.01768 | 2
2 | 120k Resistor | Digikey | B. | 100 | 0.0232 | 1
3 | 56k Resistor | Digikey | C. | 100 | 0.0232 | 1
4 | 560 Resistor | Digikey | D. | 100 | 0.0232 | 1
5 | 47nF Cap | Digikey | E. | 100 | 0.1079 | 2
6 | 22pF Cap | Digikey | F. | 100 | 0.0985 | 2
7 | 2N3904 NPN BJT | Digikey | G. | 100 | 0.139 | 1
8 | 1uH Inductor | Digikey | H. | 100 | 0.349 | 1
9 | 1uF Ceramic Cap | Digikey | I. | 100 | 0.135 | 1
10 | 2 pos Header pin | Digikey | J. | 100 | 0.0817 | 1

11 PCB (1.5"x1') | | Chopped from Projectlab | | 1 | 0.5 | 1
12 | 4Bit Fast Counter | Digikey | K. | 100 | 0.6074 | 1
13 | 14 Bit Counter | Digikey | L. | 100 | 0.5282 | 1
| | | | Total: | 2.85806
Table 3: Oscillator Bill of Materials
A. https://www.digikey.ca/product-detail/en/stackpole-electronics-inc/CF14JT10K0/CF14JT10K0CT-ND/1830374 (https://www.digikey.ca/product-detail/en/stackpole-electronics-inc/CF14JT10K0/CF14JT10K0CT-ND/1830374)
B. https://www.digikey.ca/product-detail/en/stackpole-electronics-inc/CF14JT120K/CF14JT120KCT-ND/1830401 (https://www.digikey.ca/product-detail/en/stackpole-electronics-inc/CF14JT120K/CF14JT120KCT-ND/1830401)
C. https://www.digikey.ca/product-detail/en/stackpole-electronics-inc/CF14JT56K0/CF14JT56K0CT-ND/1830393 (https://www.digikey.ca/product-detail/en/stackpole-electronics-inc/CF14JT56K0/CF14JT56K0CT-ND/1830393)
D. https://www.digikey.ca/product-detail/en/stackpole-electronics-inc/CF14JT560R/CF14JT560RCT-ND/1830344 (https://www.digikey.ca/product-detail/en/stackpole-electronics-inc/CF14JT560R/CF14JT560RCT-ND/1830344)
E. https://www.digikey.ca/product-detail/en/vishay-bc-components/K473K15X7RF5TL2/BC1082CT-ND/286704 (https://www.digikey.ca/product-detail/en/vishay-bc-components/K473K15X7RF5TL2/BC1082CT-ND/286704)
F. https://www.digikey.ca/product-detail/en/vishay-bc-components/K220J15C0GF5TL2/BC1005CT-ND/286627 (https://www.digikey.ca/product-detail/en/vishay-bc-components/K220J15C0GF5TL2/BC1005CT-ND/286627)
G. https://www.digikey.ca/product-detail/en/fairchild-on-semiconductor/2N3904BU/2N3904FS-ND/1413
H. https://www.digikey.ca/product-detail/en/murata-power-solutions-inc/11R102C/811-2018-ND/1998205
I. https://www.digikey.ca/product-detail/en/nichicon/UMT1H010MDD1TP/493-10286-1-ND/4312545
J. https://www.digikey.ca/product-detail/en/harwin-inc/M20-9990246/952-2262-ND/3728226
K. https://www.digikey.ca/product-detail/en/texas-instruments/SN74F163AN/296-14810-5-ND/562694
L. https://www.digikey.ca/product-detail/en/texas-instruments/CD74HC4060E/296-25998-5-ND/1507209

Obfuscated in these Bill of Materials is the cost of manufacturing a chassis, which presently is the largest cost of pump. We were able to print the chassis for approximately $40, or roughly double the sum total of all other component. We expect that with injection molding the per unit cost of the chassis will become insignificant.

## ISO Standard for Syringe Pumps

There is a well-established standard for syringe pumps that govern what the international

community expects from a modern syringe pump. Replicating the basic performance

characteristics forms the basis of the design parameters we are aiming for. Standard IEC 60601-

2-24, represents the international standard and CSA-C22.2 is the Canadian Standard Agency

equivalent. The standard is a rather long document and chronicles the specifics of every aspect of

any general infusion pump. Most relevant to this project is the information on volumetric flow

range, accuracy, and testing requirements for said pumps.

In the following equations Ep refers to the percentage error from the desired rate.

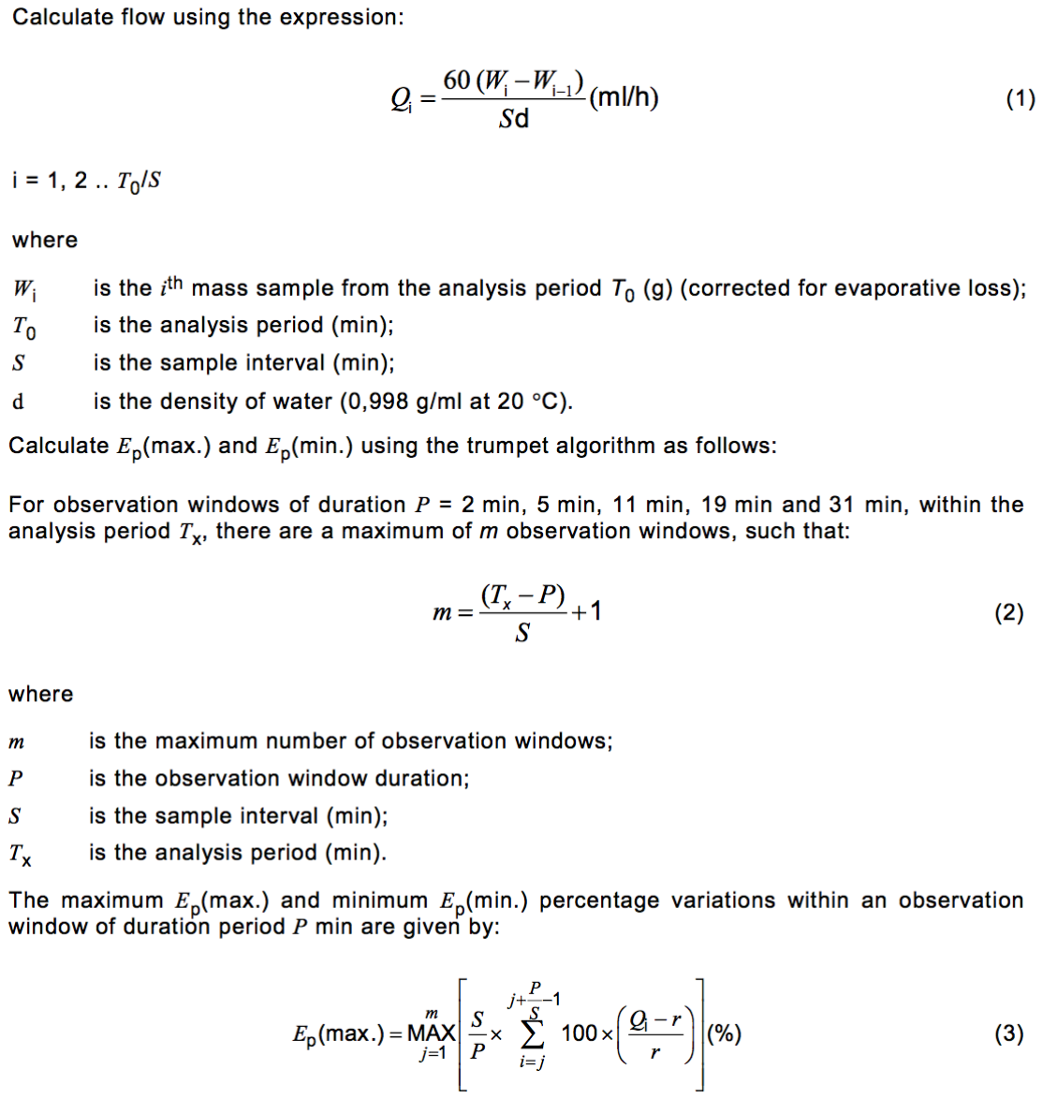
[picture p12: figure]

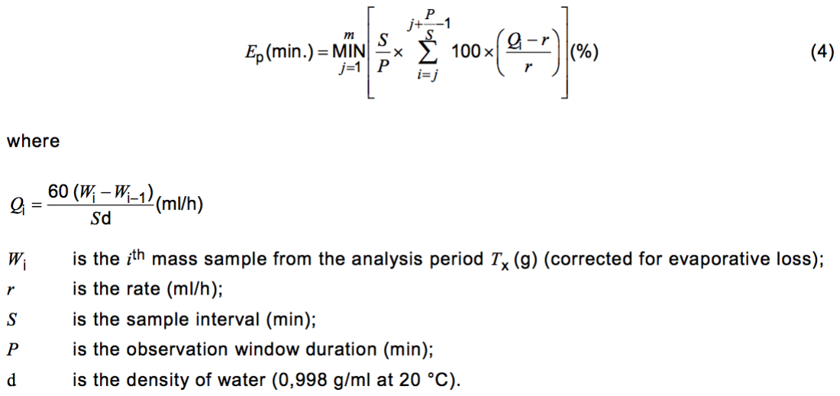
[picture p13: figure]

The trumpet algorithm represents a method for obtaining a percentage error from the variations

in flow rate, rather than an error on the measurements taken. It separates the measurement error

and the pump error, allowing an objective and comparable analysis across various pumps at

different flow rates.

The other aspect of the standard related to volumetric flow rates breaks them into two categories:

minimum and intermediate flow rates. These are not actually set by the standard, instead they are

set by the manufacturer (us), such that the minimum accuracy requirements for both rates can be

met. In addition, they outline testing apparatus, which is detailed in the long-cycle method for

verification below.

## Mechanical Drawings of Pump Chassis

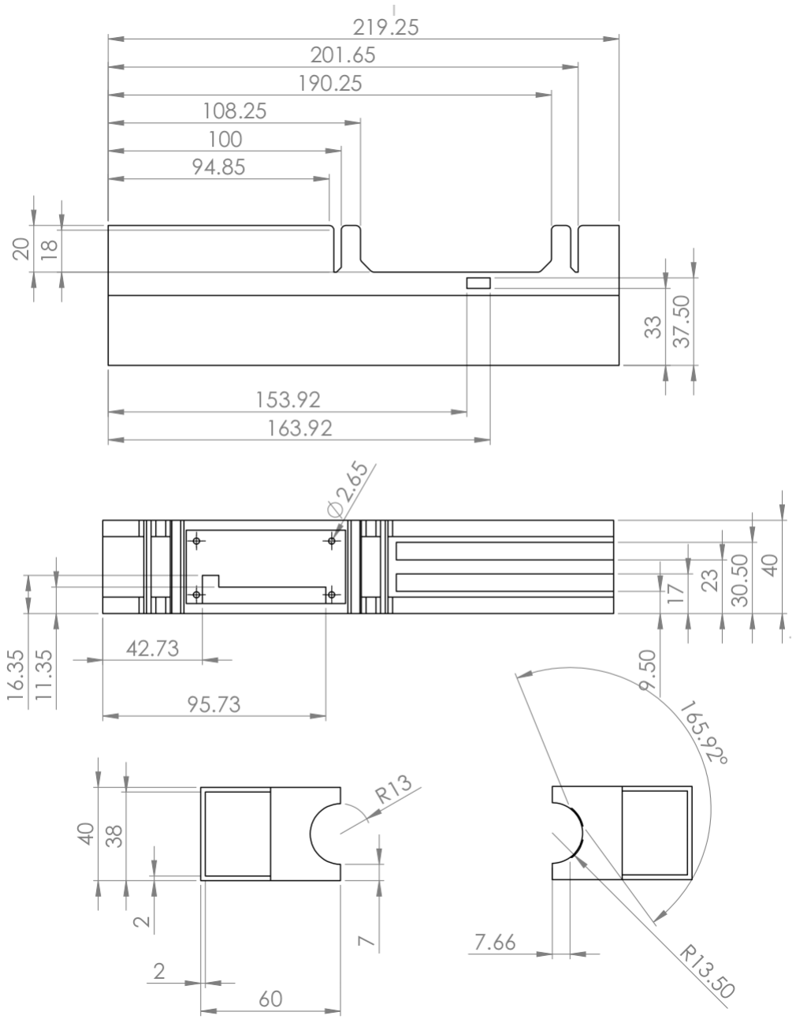
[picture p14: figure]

Figure 10: Mechanical Drawing for Pump Chassis

## Connection Diagrams for System Setup

The following diagrams show the connections for our two custom circuits, the oscillator and

driver. The RPi0 pins referenced in the diagrams follow the pin ordering labelled directly on the

prototype. All connections are made using wires with male header pins on both ends.

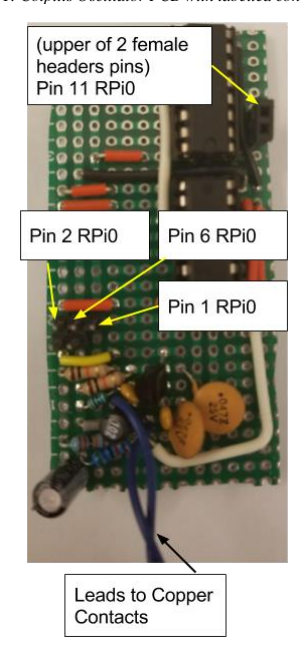
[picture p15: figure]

Figure 11: Colpitts Oscillator PCB with labelled connections

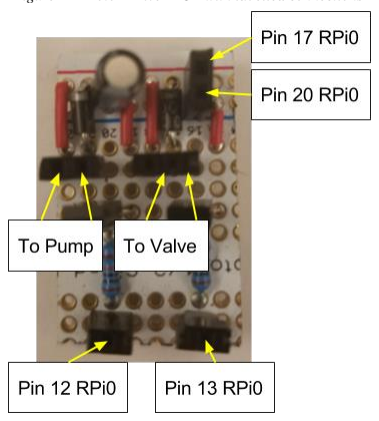
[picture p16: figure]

Figure 12: Motor Driver PCB with labelled connections

## Software Information for Project

All code for the syringe pump developed during our project can be found at:

https://github.com/akshivbansal/enph479

In order to run the Raspberry Pi Zero as headless (without using a keyboard and display, and just

connecting via SSH), we followed the reference: https://davidmaitland.me/2015/12/raspberry-pi-

zero-headless-setup/ (https://davidmaitland.me/2015/12/raspberry-pi-zero-headless-setup/)

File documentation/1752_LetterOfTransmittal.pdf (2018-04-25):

Pediatric Anesthesia Research Team Clinical Support Building, Child and Family Research Institute 950 W. 28th Avenue
Vancouver, British Columbia V5Z 4H4 Canada
January 8

th
, 2018

Dear Dr. Mark Ansermino and Dr. Guy Dumont,

In the attached document we present our Engineering Recommendation Report for our Engineering Physics Capstone Project: Development of a Low-Cost Syringe Pump for Low-Resource Anesthesia. Today, January 8th
, 2018, we officially submit this report documenting our project process, results, and future recommendations. This document is meant to serve as a guide for the continuation and expansion upon the project, which we have undertaken as part of ENPH 479, an upper level engineering project & design course. This project was planned from July-August 2017, and was developed starting September under the supervision of Dr. Jon Nakane, Dr. David Jones, and Bernhard Zender.

The report outlines our design strategy for creating a reliable, low-cost syringe pump, and the key components we designed to implement our novel approach. We also highlight the performance of our pump design and document the strengths and areas for improvement. We believe you will be most interested in the Results section, which presents the reliability and accuracy of our pump, and the Recommendations section, which outlines our suggestions for future changes and improvements to the system.

We hope the following report will be a useful reference to future students or employees who work on this project, and we suggest you keep it on file. Thank you for the opportunity to work under your guidance and to take on an exciting challenge.

Best Regards,

Akshiv Bansal | Ian Thompson

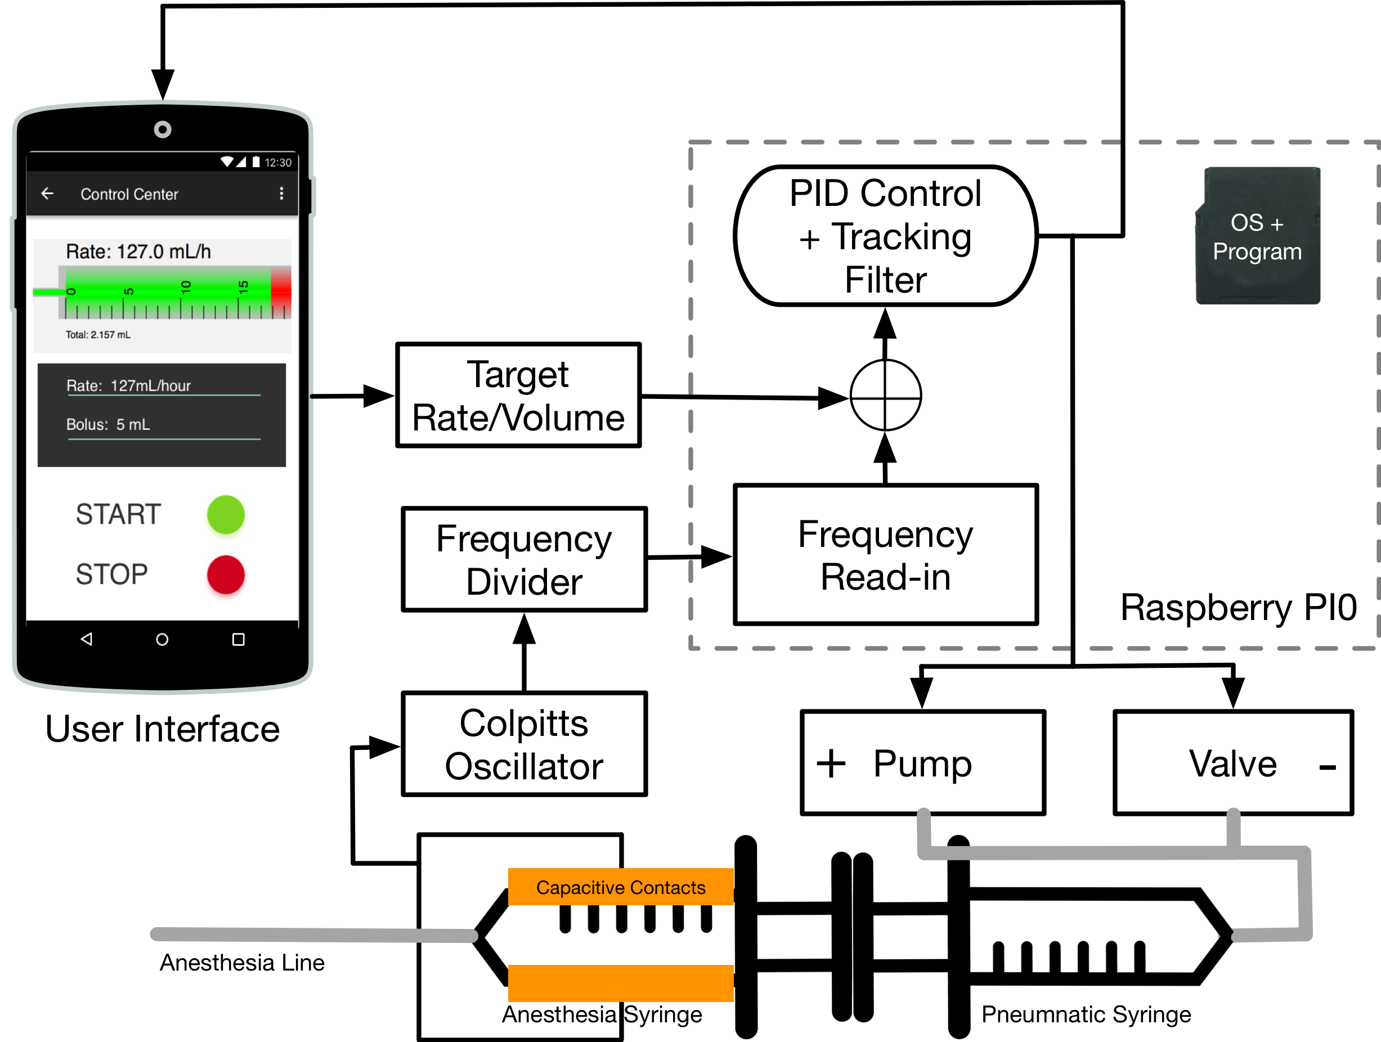
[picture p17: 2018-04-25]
documentation/figures/System Overview.png

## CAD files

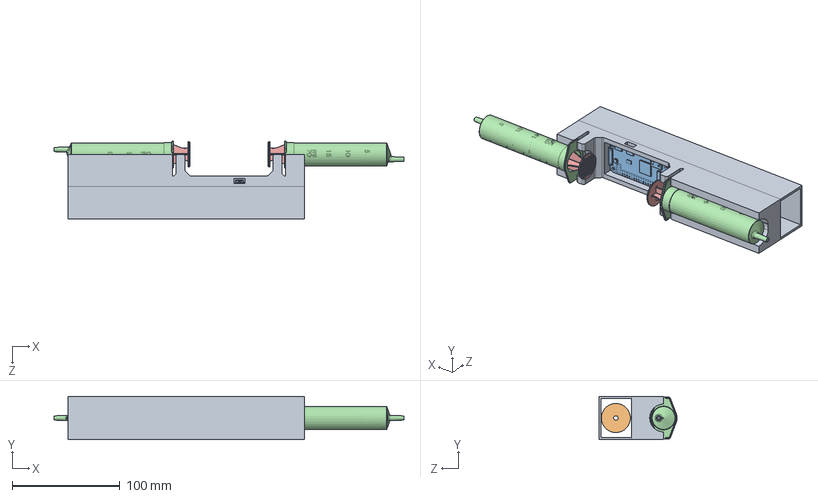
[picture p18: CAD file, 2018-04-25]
documentation/SolidWorks and 3D Printing/SyringePlus.SLDASM
324.8 x 40.0 x 72.5 mm
ImprovedSyringeHolder1
Pump
RaspberryPiZeroW
body 20ml x 2
plunger x 2
rubber plunger x 2

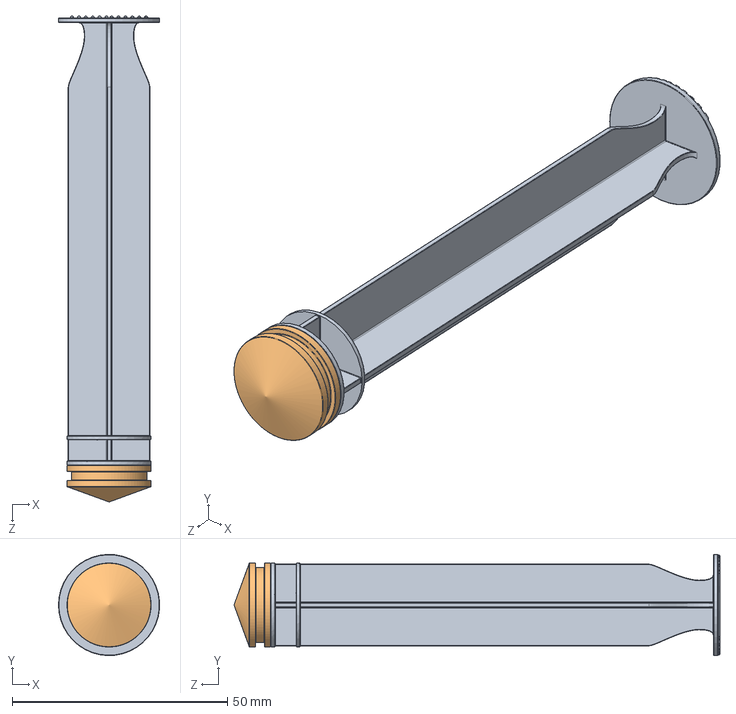
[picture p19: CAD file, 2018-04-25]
documentation/SolidWorks and 3D Printing/Plunger Assembly.SLDASM
23.5 x 23.5 x 112.8 mm
plunger
rubber plunger

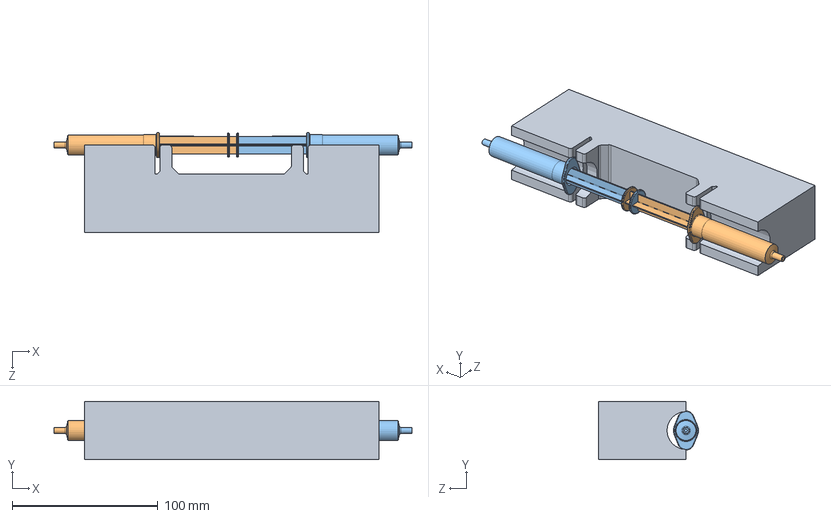
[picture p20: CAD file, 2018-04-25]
documentation/SolidWorks and 3D Printing/SmallSyringe.SLDASM
245.6 x 40.0 x 68.6 mm
OriginalSyringeHolder
5mL Syringe
SyringewFeatures

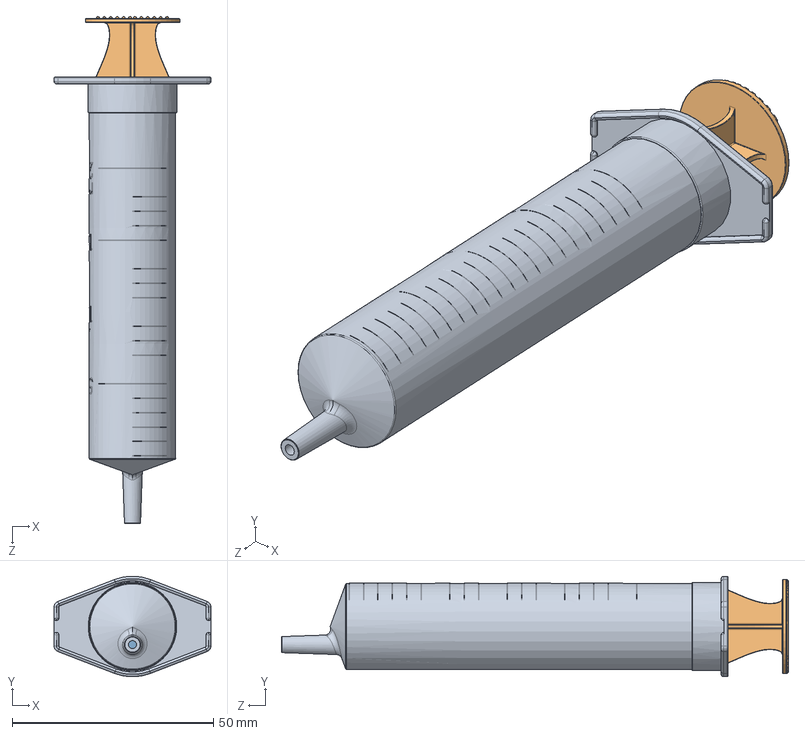
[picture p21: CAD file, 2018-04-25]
documentation/SolidWorks and 3D Printing/syringe 20ml plastipak.SLDASM
39.0 x 24.9 x 126.0 mm
body 20ml
plunger
rubber plunger

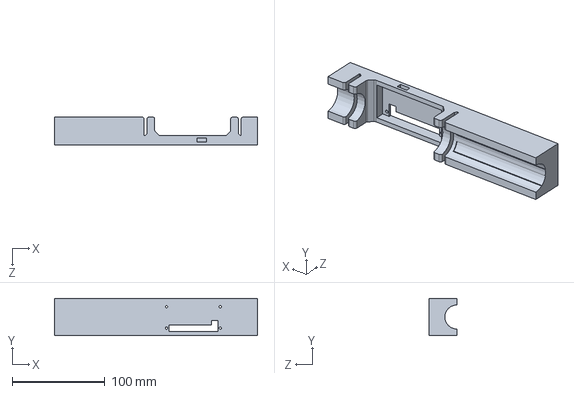
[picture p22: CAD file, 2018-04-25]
documentation/SolidWorks and 3D Printing/3D Printing/Body2.sldprt
219.2 x 40.0 x 30.0 mm

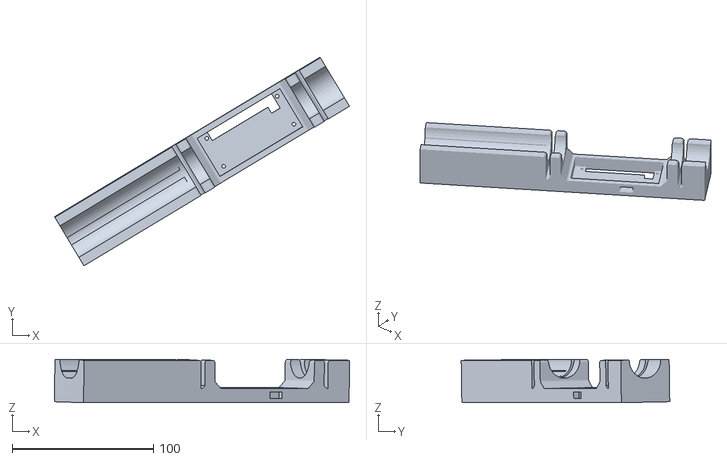
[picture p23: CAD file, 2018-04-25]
documentation/SolidWorks and 3D Printing/3D Printing/ImprovedSyringeHolder1_export.stl
208.8 x 147.7 x 30.7

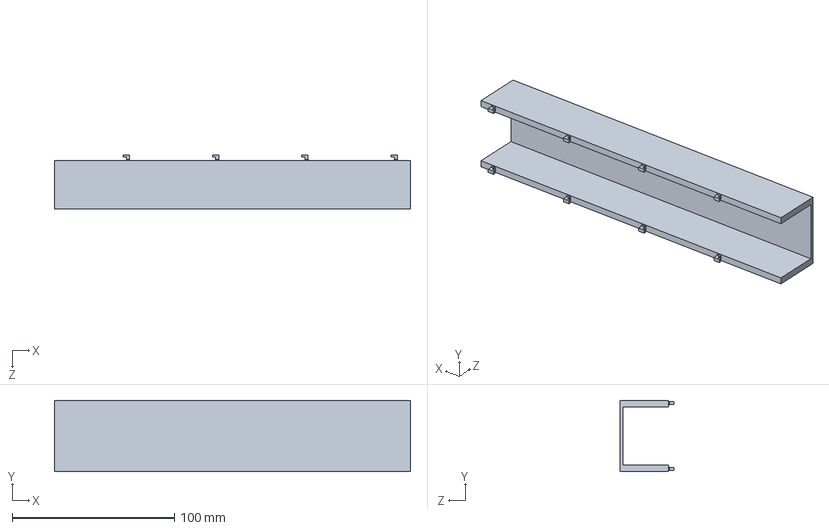
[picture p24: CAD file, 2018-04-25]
documentation/SolidWorks and 3D Printing/New and Sealed/Body1.sldprt
219.2 x 44.0 x 33.5 mm

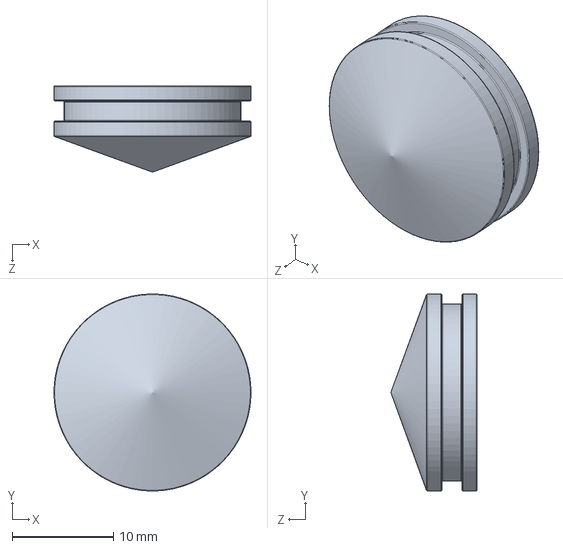
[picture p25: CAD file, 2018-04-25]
documentation/SolidWorks and 3D Printing/rubber plunger.SLDPRT
19.5 x 19.5 x 8.55 mm

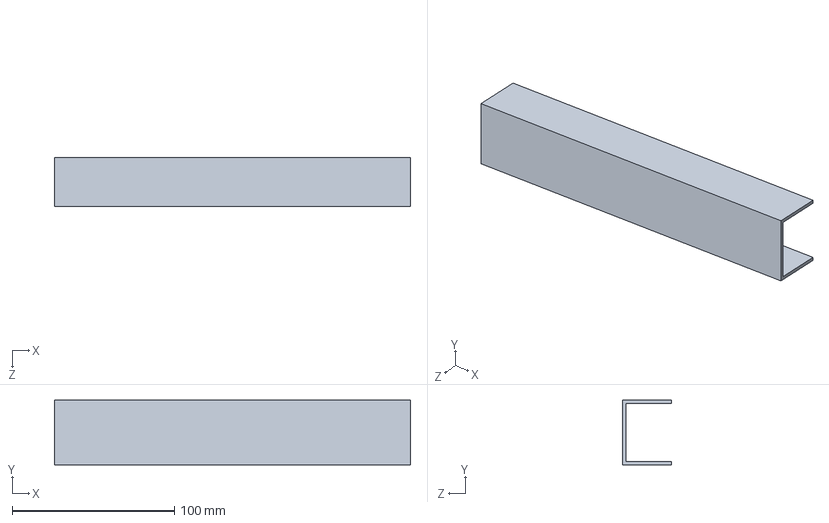
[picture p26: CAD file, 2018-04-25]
documentation/SolidWorks and 3D Printing/3D Printing/Body1.sldprt
219.2 x 40.0 x 30.0 mm

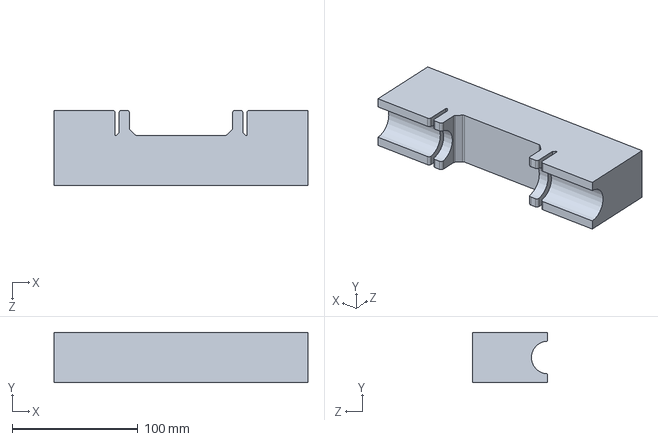
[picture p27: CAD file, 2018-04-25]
documentation/SolidWorks and 3D Printing/OriginalSyringeHolder.SLDPRT
202.0 x 40.0 x 60.0 mm

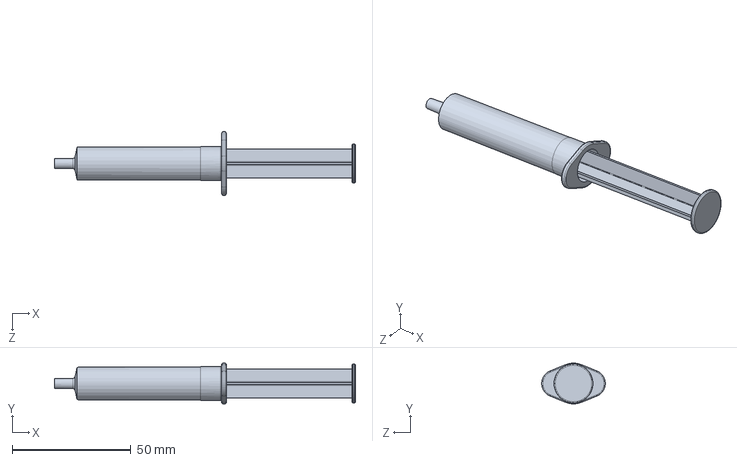
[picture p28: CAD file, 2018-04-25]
documentation/SolidWorks and 3D Printing/SyringewFeatures.SLDPRT
126.7 x 17.2 x 26.8 mm

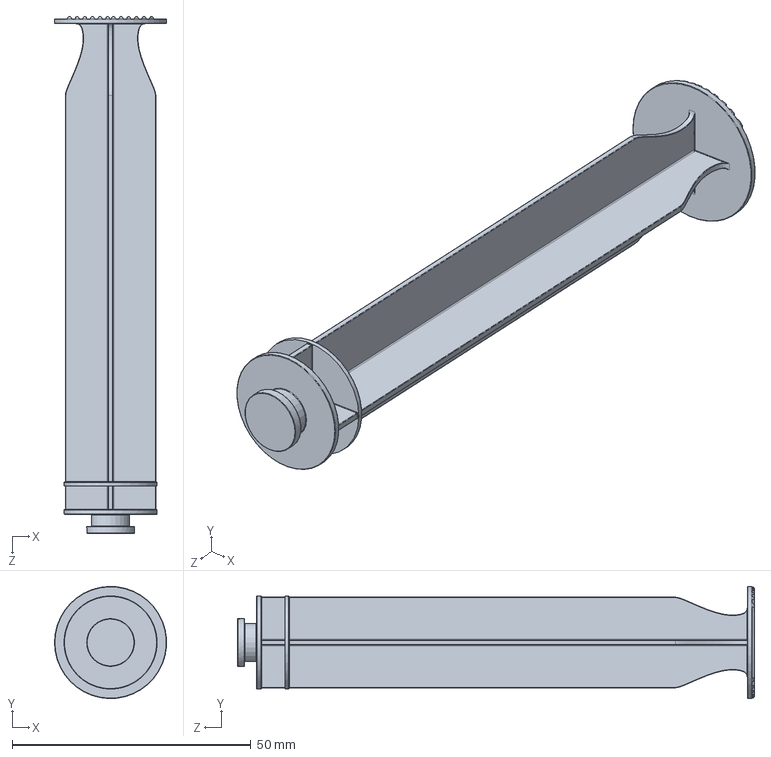
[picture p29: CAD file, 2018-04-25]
documentation/SolidWorks and 3D Printing/plunger.SLDPRT
23.5 x 23.5 x 108.3 mm

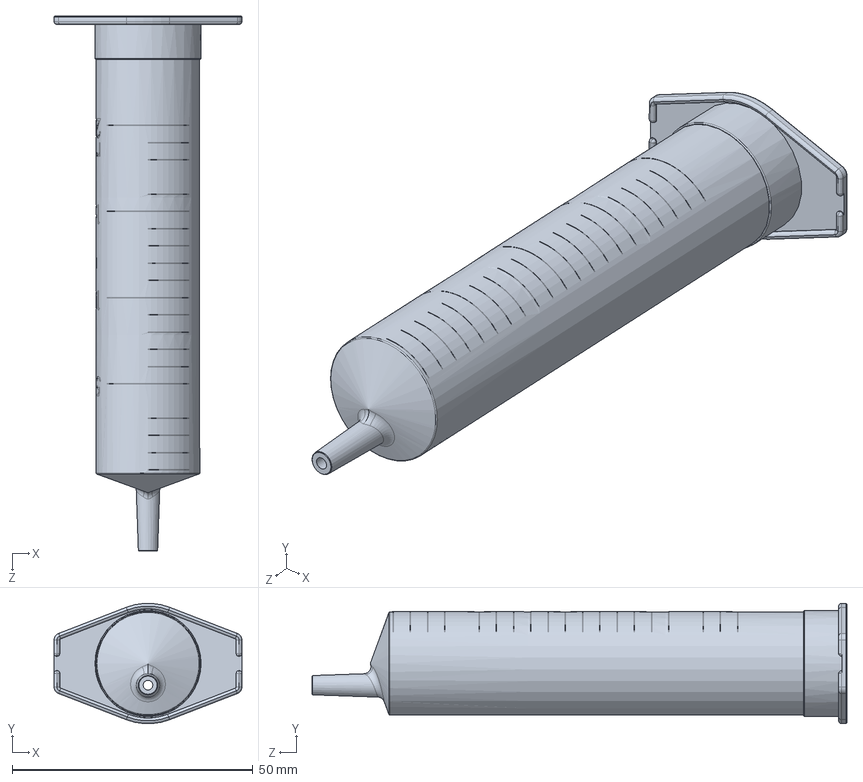
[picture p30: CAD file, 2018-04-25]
documentation/SolidWorks and 3D Printing/body 20ml.SLDPRT
39.0 x 24.9 x 111.0 mm

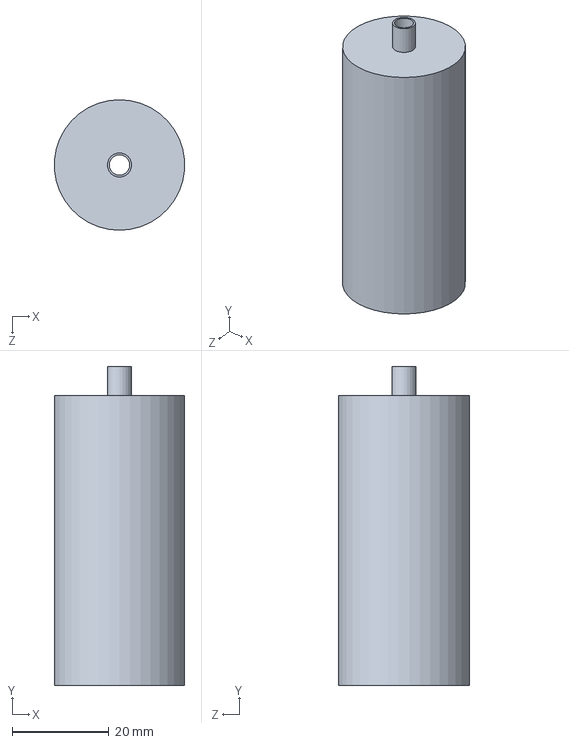
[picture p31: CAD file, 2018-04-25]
documentation/SolidWorks and 3D Printing/Pump.SLDPRT
26.9 x 66.0 x 27.0 mm

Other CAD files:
documentation/SolidWorks and 3D Printing/New and Sealed/Body2.sldprt
documentation/SolidWorks and 3D Printing/3D Printing/ImprovedSyringeHolder2.STL
documentation/SolidWorks and 3D Printing/SyringeHolder.SLDPRT
documentation/SolidWorks and 3D Printing/RaspberryPiZeroW.SLDPRT
documentation/SolidWorks and 3D Printing/3D Printing/ImprovedSyringeHolder1.STL
documentation/SolidWorks and 3D Printing/5mL Syringe.SLDPRT
documentation/SolidWorks and 3D Printing/ImprovedSyringeHolder1.SLDDRW
documentation/SolidWorks and 3D Printing/ImprovedSyringeHolder1.SLDPRT

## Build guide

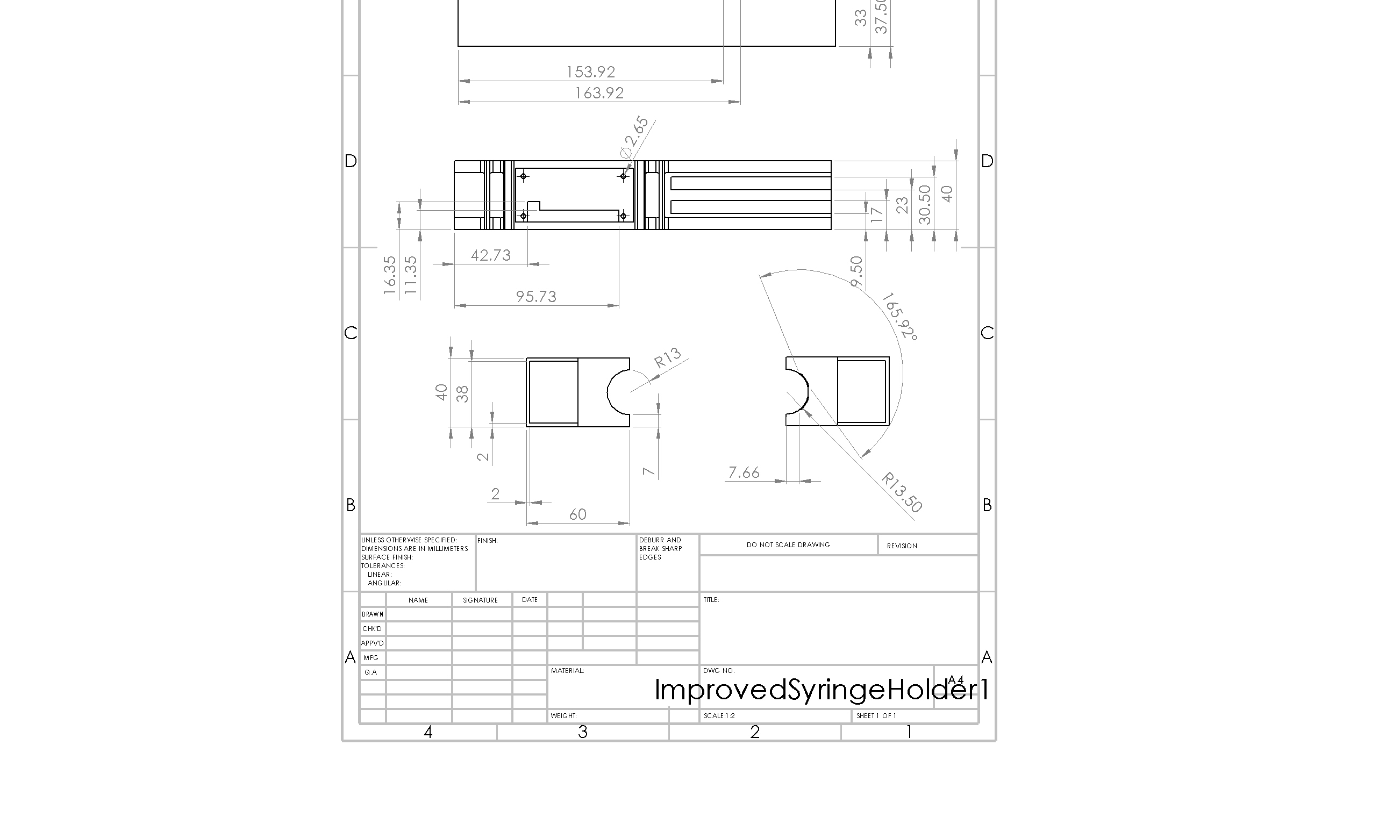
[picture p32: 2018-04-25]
documentation/SolidWorks and 3D Printing/ImprovedSyringeHolder1.JPG

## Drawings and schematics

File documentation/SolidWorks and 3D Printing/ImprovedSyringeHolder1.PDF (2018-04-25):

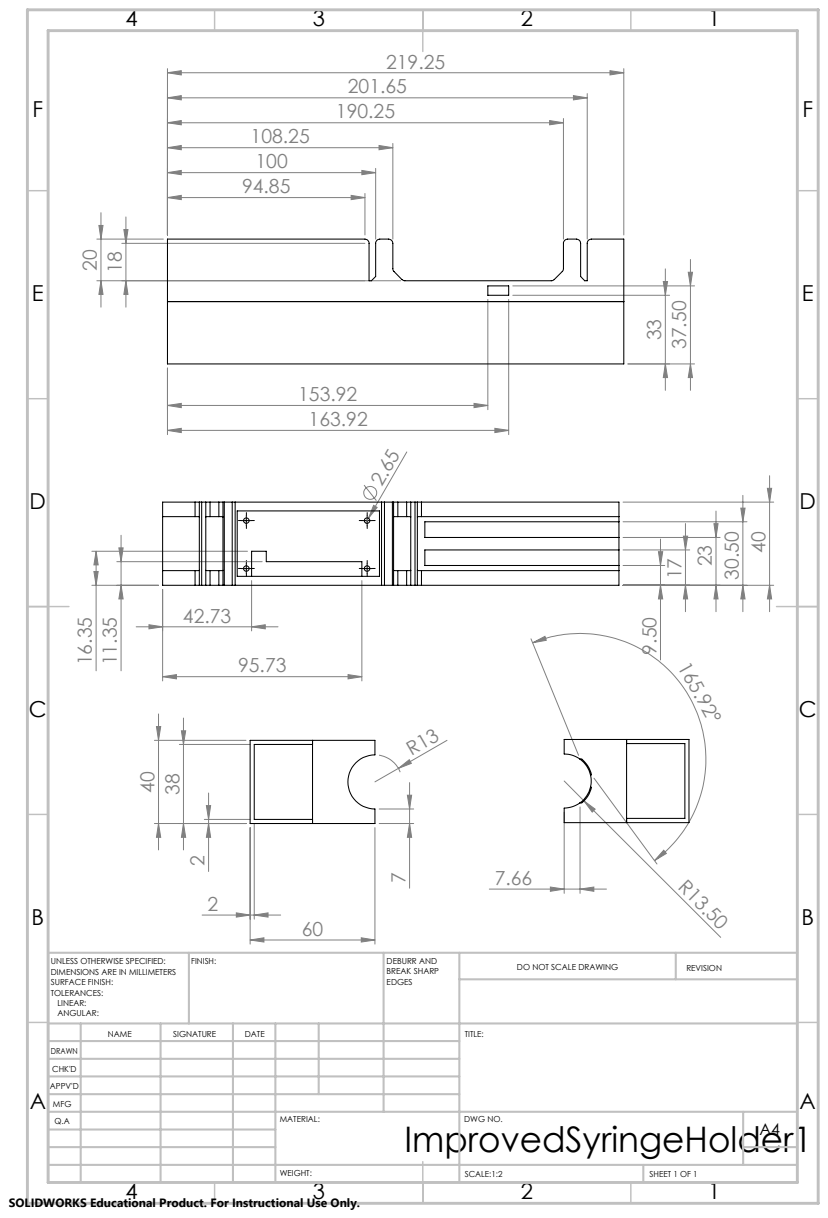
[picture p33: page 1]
FINISH:; DEBURR AND; BREAK SHARP; DO NOT SCALE DRAWING; REVISION; SCALE:1:2; SHEET 1 OF 1

UNLESS OTHERWISE SPECIFIED:
DIMENSIONS ARE IN MILLIMETERS
SURFACE FINISH:
TOLERANCES:
LINEAR:
ANGULAR:

NAME | SIGNATURE | DATE | | | | TITLE:

DRAWN
CHK'D
APPV'D
MFG
Q.A | | | | MATERIAL: ImprovedSyringeHolder1 | DWG NO. | A4

SOLIDWORKS Educational Product. For Instructional Use Only.

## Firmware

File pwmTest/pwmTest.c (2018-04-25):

/*
* PID Test Code for RPi0
* Written By: Akshiv Bansal & Ian Thompson
* Project: $20 Syringe Pump for Digital Health Innovation Lab
*/

#include <stdio.h>
#include <stdlib.h>
#include <errno.h>
#include <time.h>
#include <signal.h>
#include <string.h>
#include <stdint.h>
#include "setup.h"
#include "interrupt.h"

// Constants for error control
#define KD 0   							// Derivative Control Constant 
#define KP 2  							// Proportional Control Constant 
#define KI 1							// Integral Control Constant 
#define WINDUP_THRESHOLD 200 			// Used to avoid sudden changes
// Constants for pump driving
#define STEP_UP 20						// Per cycle of the control loop
#define STEP_UP_MAX 25
#define STEP_DOWN 20
#define STEP_DOWN_MAX 50
#define PWM_LIMIT 450
#define BLOWOFF_TIME 100 				// Controls the duration of valve opening for releasing pressure

void exitHandler(int);
int getError(int);
int controlPump(int, int, int);
void drivePump(int, int);
double round(double);

volatile int timeDiff = 0;

int main(int argc, char **argv) {
	// Read in the specified rate and volume parameters
	if(argc != 4){
		fprintf(stderr, "Error: Need to input arguments as Flow rate, then total volume.\n");
		exit(-1);
	}
	int power = atoi(argv[3]); // Get power to push the pump with
	// Check to make sure the power is in range
	if(power < PWM_MIN || power > PWM_MAX){
		fprintf(stderr, "Error: Power target out of range.\n");
		exit(-1);
	}
	int rate = atoi(argv[1]); // Get flow rate in uL/h
	// Check to make sure the flow rate is in range
	if( rate < MIN_RATE || rate > MAX_RATE ){
		fprintf(stderr, "Error: Flow rate out of range.\n");
		exit(-1);
	}
	int volume = atoi(argv[2]); // Get total volume goal in uL
	// Check to make sure the volume is in range
	if(volume < MIN_VOLUME || volume > MAX_VOLUME){
		fprintf(stderr, "Error: Volume target out of range.\n");
		exit(-1);
	}

	// Setup shutdown protocol
	signal(SIGINT, exitHandler);

	// Configure Raspberry Pi
	rPiSetup();
	delay(1000);

	// Set up targets for control
	int target = setTarget(rate);
	int totalTarget = setTotal(volume);
	int error;
	int total = 0;
	
	// If testing pump response to different driving PWM, this mode simply lets the air pump 
	// run at a specified PWM
	digitalWrite(VALVE_PIN,HIGH);
	delay(1000);
	pwmWrite(PUMP_PIN,power);
	
	// Display the setup info, then wait to let feedback counter settle 
	// Without this delay, the first feedback value is often incorrect and large
	printf("Target Rate: %d, Target Total: %d\n\n", target, totalTarget);
	delay(5000);

	// Run this loop until we have infused the desired total volume
	while(total < totalTarget){
		printf("Feedback value: %d\n",timeDiff);

	}

	// Once infusion is finished, turn all pumping off
	pwmWrite(PUMP_PIN, PWM_MIN);
	digitalWrite(VALVE_PIN, LOW);
	return 0;
}

// Handles the proper shutdown of the code, setting the pump off and valve open when ctrl+C is
// used to stop the code.
void exitHandler(int sig){
	digitalWrite(VALVE_PIN,LOW);
	pwmWrite(PUMP_PIN,PWM_MIN);
	exit(0);
}

// getError: Takes the target count value per measurement interval, then counts over the 
// specified interval to determine the error over the interval. The error is returned
int getError(int target){
	int change = 0;
	int valOld = timeDiff;

	// Wait for a change in the feedback read-in then record this change
	while(timeDiff == valOld){}
	change = -1*(timeDiff - valOld);
	// Maybe add some sort of jump rejection to deal with setpoint shifts from movement
	
	// Calculate the error by comparing the real and target change
	int error = change - target;
	printf("Change: %d\n", change);
	return error;
}

// controlPump: Takes the error over an interval and controls the air pump and valve in
// response to this error. Returns the accumulated total count. 
int controlPump(int error, int total, int target){
	static int integralError = 0;
	static int prevError = 0;

	// Keep a running log of the total infusion by counting up 
	total = total - (error - target);

	// Calculate the derivative and integral error (with wind-up limits)
	int derivError = error - prevError;
	integralError = integralError + error; 
	if (integralError > WINDUP_THRESHOLD){
		integralError = WINDUP_THRESHOLD;
	} else if(integralError < -1*WINDUP_THRESHOLD){
		integralError = -1*WINDUP_THRESHOLD;
	}

	// Calculate & output the final correction based on the errors
	int correction = KP*error + KD*derivError + KI*integralError;
	printf("Error: %d, Integral Error: %d, Correction: %d\n", error, integralError, correction);	
	drivePump(correction, target);
	prevError = error;
	return total;
}


// drivePump: controls the valve and pump to correctly react to a correction
void drivePump(int correction, int target){
	static int pwmCurrent 	= 0;
	int step = 0;

	// Based on the correction values we apply different actions to the pump
	if(correction < 0){
	// If the pump is lagging, we need to pump more to catch up as we are lagging
		printf("Push\n\n");
		
		// Increase the pumping proportionally to the correction, up to a limit
		step = -1*correction;
		if(step > STEP_UP_MAX){
			step = STEP_UP_MAX;
		}
			pwmCurrent = pwmCurrent + step; 
		// Apply a limit on the maximum pump speed
		if (pwmCurrent > PWM_LIMIT){
			pwmCurrent = PWM_LIMIT;
		}
		pwmWrite(PUMP_PIN, pwmCurrent);
		digitalWrite(VALVE_PIN, HIGH);
	} else if (correction > 1000*target){
	// If the pump is moving too fast we open the valve to release pressure
		printf("Blowoff\n\n");
		pwmWrite(PUMP_PIN, PWM_MIN);
		digitalWrite(VALVE_PIN, LOW);
		delay(BLOWOFF_TIME);
		digitalWrite(VALVE_PIN, HIGH);
		// Reset the pump speed after blowoff
		pwmCurrent = 0;
	} else {
	// If the pump is slighly too fast we slow the pump speed, proportionally to the correction
		step = correction;
		if(step > STEP_DOWN_MAX){
			step = STEP_DOWN_MAX;
		}
		printf("Wait\n\n");
		pwmCurrent = pwmCurrent - step;
		// Ensure the pump speed doesn't drop below zero
	  	if(pwmCurrent < 0){
			pwmCurrent = 0;
		}
		pwmWrite(PUMP_PIN, pwmCurrent);
		digitalWrite(VALVE_PIN, HIGH);
	}
	printf("PWMCurrent: %d\n", pwmCurrent);
	return;
}

// Rounds to nearest integer
double round(double number){
	return (number - floor(number) >= 0.5) ? ceil(number) : floor(number);
}

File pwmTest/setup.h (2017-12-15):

#ifndef SETUP_H_INCLUDED
#define SETUP_H_INCLUDED

#include <math.h>
#include <wiringPi.h>

// Setup pin configurations
#define LOW 0
#define HIGH 1
#define COUNTER_PIN 0
#define PUMP_PIN 1
#define VALVE_PIN 2
#define PWM_MIN 0
#define PWM_MAX 1024


// Configure syringe information
#define SYRINGE_MAX_READING 2153750
#define SYRINGE_MIN_READING 2117780 // Need to set infusion limits based on known limits of values
#define SYRINGE_VOLUME_UL 22000
#define READING_PER_UL (double) (SYRINGE_MAX_READING-SYRINGE_MIN_READING)/SYRINGE_VOLUME_UL //Estimated as Linear
#define MAX_RATE 200000
#define MIN_RATE 10000
#define MAX_VOLUME 20000
#define MIN_VOLUME 1000

#define SAMPLING_NUMBER 250
#define HR_TO_SEC 0.000277778

// rPiSetup: Sets up WiringPi, Interrupt, and Output Pins for proper board operation
// The board is setup with the pump off, interrupt enabled and valve open.
void rPiSetup(void);


// setTarget: Takes the specified rate, volume, and averaging interval, and returns the 
// target count value per measurement interval 
int setTarget(int rate);


// setTotal: Takes the specified rate, volume, and averaging interval, and returns the 
// total target count value over the duration of the pump infusion
int setTotal(int volume);

#endif

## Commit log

2017-10-22 Fixing wiringPi initialization errors
2017-10-28 Changed the code to sample period based off new downsampled oscillator
2017-11-13 Added exit handling, and basic code to drive pump while reading out status
2017-11-13 Adding power control from command line
2017-12-15 Made some changes to error calculation and tried to implement varying adjustments to pumping speed based on error magnitude
2018-04-25 Added SolidWorks Files
    [5mL Syringe.SLDPRT, Body1.sldprt, Body2.sldprt, ImprovedSyringeHolder1.SLDDRW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]
